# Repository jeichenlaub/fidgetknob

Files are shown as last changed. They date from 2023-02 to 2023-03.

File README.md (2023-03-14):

# Fidget Knob



Hello! Thanks for your interest in the Fidget Knob instrumented fidget object and research platform. This README serves as a general guide (or points you to other built-in and external guides) with all you need to know to construct and run your own implementation of the Fidget Knob. As such, I do implore you to read it carefully. 

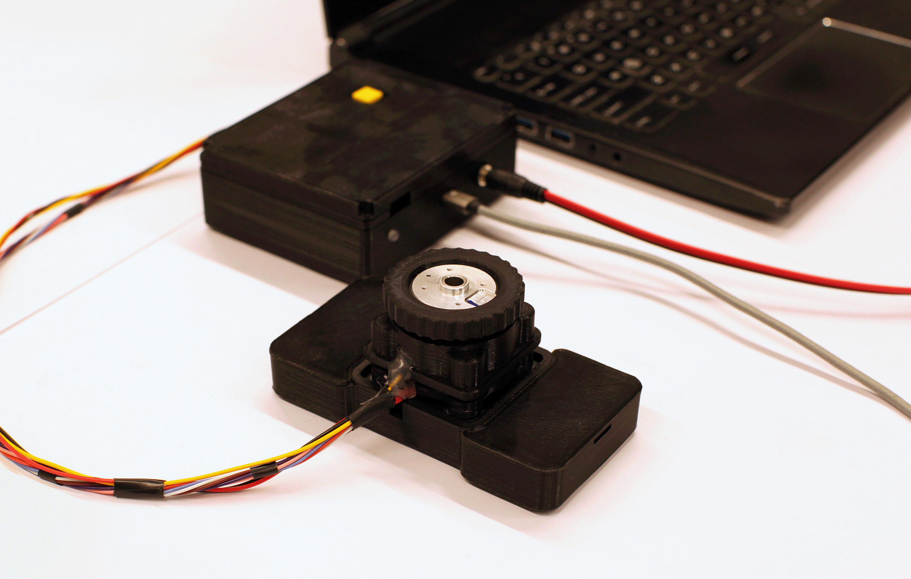
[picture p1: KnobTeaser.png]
Hero shot of the device


The overall system is pretty simple: a brushless DC (BLDC) motor has its angular position (and velocity) detected by a magnetic field sensor, which is fed into a ‘field oriented control’ algorithm to generate different haptic sensations and virtual detents. For those experienced in microelectronics, feel free to diverge from this guide when useful. For those still learning, hopefully this guide can take you step by step.

This GitHub repository contains all the files required from both a software and hardware perspective. It contains the following elements, and is organized in GitHub in a similar manner: 

# File Organization
 1. CAD\
&emsp;a. Part Files\
&emsp;b. Knob Assembly Instructions\
&emsp;c. Knob BOM\
&emsp;d. Knob Pics 
 2. Hardware\
&emsp;a. Electronics Assembly Instructions\
&emsp;b. Electronics BOM\
&emsp;c. Electronics Pics
 3. libraries\
&emsp;a. requirements.txt
 4. FidgetKnob_CustomCalibration.ino
 5. FidgetKnob_Main.ino
 6. FidgetKnob_DataLogging.pde
 7. LICENSE
 8. README

# Firmware and Software

The core of this project is a single Arduino .ino file. The software can be initiated in 2 modes: If one holds down the mode select button on startup (until the LED blinks blue 3 times), the Fidget Knob runs independently and without data logging enabled through Processing. If one does not hold any buttons, the Fidget Knob will remain uninitialized until it receives a timestamp from Processing, and it will flash green rapidly to indicate successful boot. While Arduino/C++ may not be the most robust programming language and platform for advanced works, it is relatively approachable for beginner and intermediate coders and thus suits our use case. 

This main .ino is supported by multiple libraries (found in requirements.txt) that are REQUIRED for the proper functioning of the software. These libraries are also included in the 'libraries' folder due to their permissive licensing rules.

**BEFORE RUNNING** the Fidget Knob, one must calibrate it with the included calibration program *FidgetKnob_CustomCalibration.ino.* Please note this calibration program is not great, and one should run it multiple times to get an average value for the "electrical offset." This value then needs to be changed in FidgetKnob_Main.ino file. The calibration program also should determine the amount of electrical pole pairs your motor has, but I find it best to do this using instructions on SimpleFOC's page for getting started (https://docs.simplefoc.com/example_from_scratch), or use the manufacturer claim. By setting this as a fixed value in the program, the 'electrical offset' calibration becomes more accurate. One can also use SimpleFOC's built in offset calibration programs, but these seem to yield equally inaccurate results with this specific hardware setup.

Datalogging is handled over serial connection with a parallel Processing scripts (FidgetKnob_DataLogging.pde). One can utilize this script either through the Processing IDE (running on a PC connected to the Fidget Knob via USB) or through the standalone application also included on this GitHub. Please note that certain parameters need to be adjusted (such as data file name and COM port of device) per instance of the Fidget Knob, so we highly recommend the former option of using the IDE. Complete instructions for the code, it's variables, and it's functions are found within the Processing file itself.

## Future Developments
We welcome any iterations that researchers and independent users wish to make for this prototype. We ask that you record these changes in a systematic way for future users.

A clear first point of future development is to enable either local or wireless data logging to untether the device from a laptop. The ESP32 platform is readily equipped to do so, and it was outside the scope of my own research.

The calibration programs are notoroiusly finicky and not fully functional. These need to be improved for this hardware combination to enable better off-the-shelf usage.

*insert more here when discovered*

# CAD
To build a full Fidget Knob, one will require a number of 3D printed parts to make up a housing for the knob and a container for the electronics. All of these files have been provided (as Solidworks .sldprt and print-ready .stl files) in the CAD folder.

While assembly of the parts is pretty straightforward, we have included a step by step instructions (KnobAssembly) and a bill of materials in the relevant folders.

# Potential FAQ and Troubleshooting
To save the general public some hassle, I have compiled a list of the largest and most crucial errors that I encountered while creating this device, as well as their solutions. This section can be a resource if something goes wrong, most specifically with compiling software and building out the electronic components of the project. 

*insert more here when discovered*

# Acknowledgments

This project is more or less a branch of Scott Bezek’s ‘[SmartKnob](https://github.com/scottbez1/smartknob)’ project , which is itself just a custom implementation of the [SimpleFOC](https://simplefoc.com/) library ([https://github.com/simplefoc](https://github.com/simplefoc)). We are greatly indebted to both of those projects and communities.

This project was developed during my term as a research employee at the faculty of Industrial Design Engineering at the Technical University of Delft in Delft, the Netherlands. As the project is based in open source software, no intellectual property rights are derived by the University.

# License and Citation

This Fidget Knob platform is designed for use in a research setting, ideally to enable better study of fidgeting behaviors and to help create target design interventions in this space. For those who use the Fidget Knob in their research, please cite this project with the following DOI: 10.5281/zenodo.7732484.

This project is licensed under Apache v2 (software, electronics, documentation) and Creative Commons Attribution 4.0 (hardware/mechanical) (see [LICENSE.txt](https://github.com/jeichenlaub/fidgetknob/blob/main/LICENSE)  and  [Creative Commons](https://creativecommons.org/licenses/by/4.0/)).
```
'fidgetknob' Copyright 2023 - John Anders Eichenlaub 

Licensed under the Apache License, Version 2.0 (the "License");
you may not use this file except in compliance with the License.
You may obtain a copy of the License at

		http://www.apache.org/licenses/LICENSE-2.0
		
Unless required by applicable law or agreed to in writing, software
distributed under the License is distributed on an "AS IS" BASIS,
WITHOUT WARRANTIES OR CONDITIONS OF ANY KIND, either express or implied.
See the License for the specific language governing permissions and
limitations under the License.
```

> Written with [StackEdit](https://stackedit.io/).

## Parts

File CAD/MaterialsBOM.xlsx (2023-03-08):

Item NO. | Part Name | Quantity | Example Link
----- | KNOB ASSEMBLY | ------ | MotorAssembly.sldasm
1 | FK_MT7601Holder | 1 | CAD
2 | FK_AssmBasePlate | 1 | CAD
3 | FK_TableBase | 1 | CAD
4
5 | FK_BLDCMount | 1 | CAD
6 | FK_AssmPeg | 4 | CAD
7 | FK_KnobGrip | 1 | CAD
8 | Super Glue (1g) | 1 | Your preferred brand
9 | Magnet (2x8mm dia.) | 8 | Neodymium magnet
10 | 30diax1mm washer | 52 | https://www.bilcastors.co.uk/product/flat-washer-10mm-internel-30mm-outter-x-1mm-thick/
11 | M3 hex head bolt, 10mm | 4
12 | Rubber Feet | 4-8 | https://www.westfloridacomponents.com/HW074/Clear+Hemispherical+Self-Adhesive+Rubber+Feet+Small+Bumpons+7.9++X++2.2mm.html
----- | Electronics Box | ------ | ElectronicsBox.sldasm
1 | FK_ElectronicsBox | 1
2 | FK_ElectronicsLid | 1
3 | FK_ButtonArm | 1
4 | Super Glue (1g) | 1 | Your preferred brand

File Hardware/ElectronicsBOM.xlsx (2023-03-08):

ID Number | Short Name | Official Name | Qty. | Links:
1 | Breadboard | Self-adhesive solderless breadboard, 0.1inch pitch |  | https://www.sparkfun.com/products/12002
2 | Breadboard | Self-adhesive solderless breadboard, 0.1inch pitch |  | "
3 | Motor Driver | TMC6300 BOB |  | https://www.top-electronics.com/en/breakout-board-with-tmc6300
4 | Microcontroller | DoIt Devkit ESP32 v1 |  | https://nl.aliexpress.com/item/32928267626.html
5 | BLDC Motor | Brushless DC motor TYPE A, 260 KV, 7 pole pair, 32mm diameter |  | https://nl.aliexpress.com/item/1005004385440039.html
6 | Magnetic Encoder | MT6701 (MagnTek) BOB |  | https://nl.aliexpress.com/item/1005004216051325.html?gatewayAdapt=glo2nld
7 | Resistor 1 | 560 ohm
8 | Resistor 2 | 560 ohm
9 | 24AWG coated wire (65cm) |  | 20
10 | Mode Switch Button | Basic 4 pin button (omron b3f) |  | https://www.sparkfun.com/products/10302
11 | Indicator LED | 4 Pin translucent RGB LED |  | https://nl.aliexpress.com/item/1005004948808839.html?
12 | DC Supply Jack | Standard barrel jack, 2 output pins version |  | https://nl.aliexpress.com/item/4000648876487.html?curPageLogUid=6nWUYysneIPZ
13 | Power Supply | AC to DC power supply, 10v 2 amp |  | https://nl.aliexpress.com/item/1005003090719320.html?curPageLogUid=LcfFNOlMRHSw
14 | Micro USB cable | 1m Micro-USB to USB A cable |  | https://nl.aliexpress.com/item/4000115356367.html?scm_id=1007.13339.291025.0&scm-url=1007.13339.291025.0
15 | Wisher jumper wire kit |  |  | https://www.retroamplis.com/Jumper-set-350-pcs

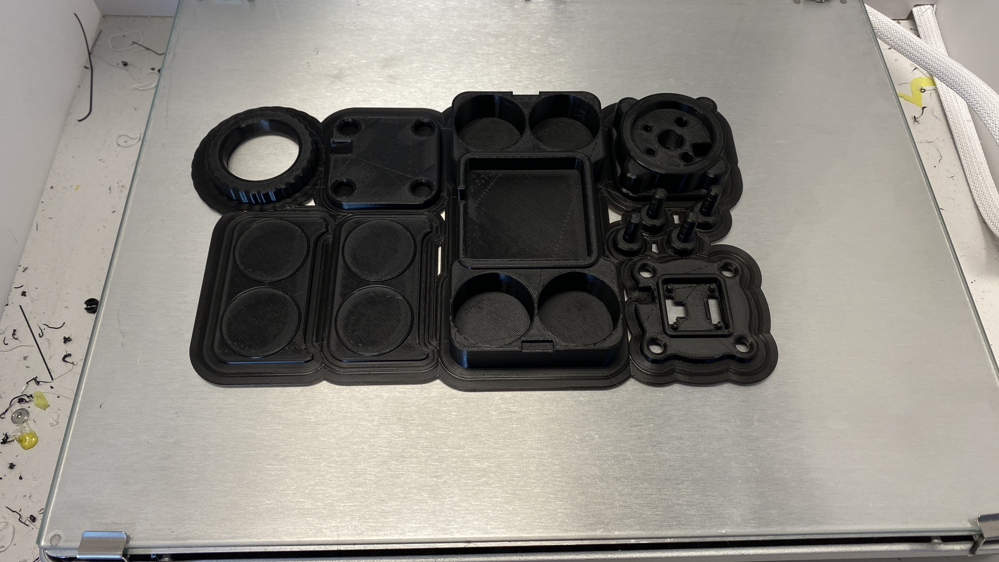
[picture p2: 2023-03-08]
CAD/KnobPics/Parts_OnPrinter.jpg

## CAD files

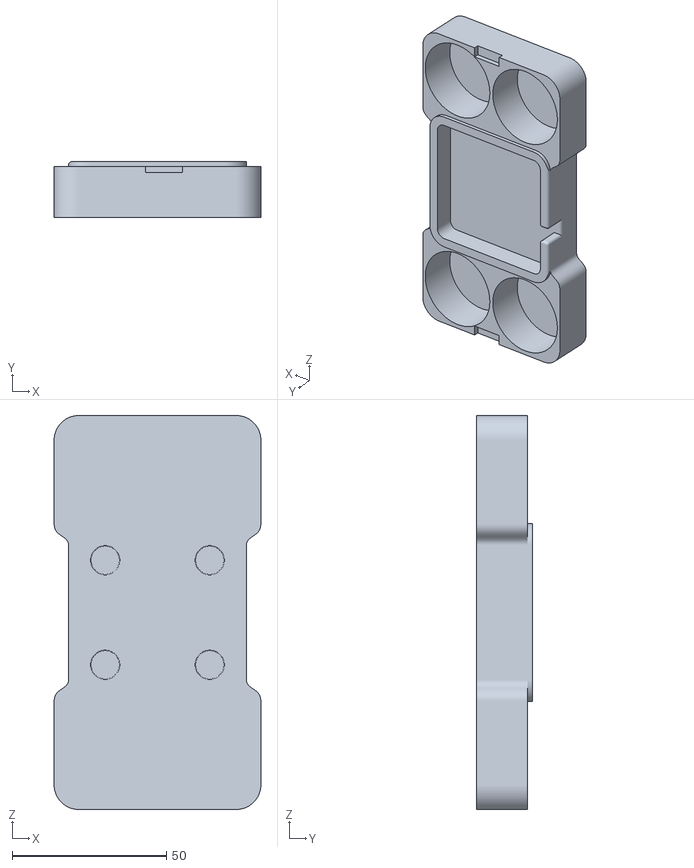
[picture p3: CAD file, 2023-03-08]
CAD/MotorAssembly - FK_TableBase-1.STL
67.0 x 18.0 x 127.7

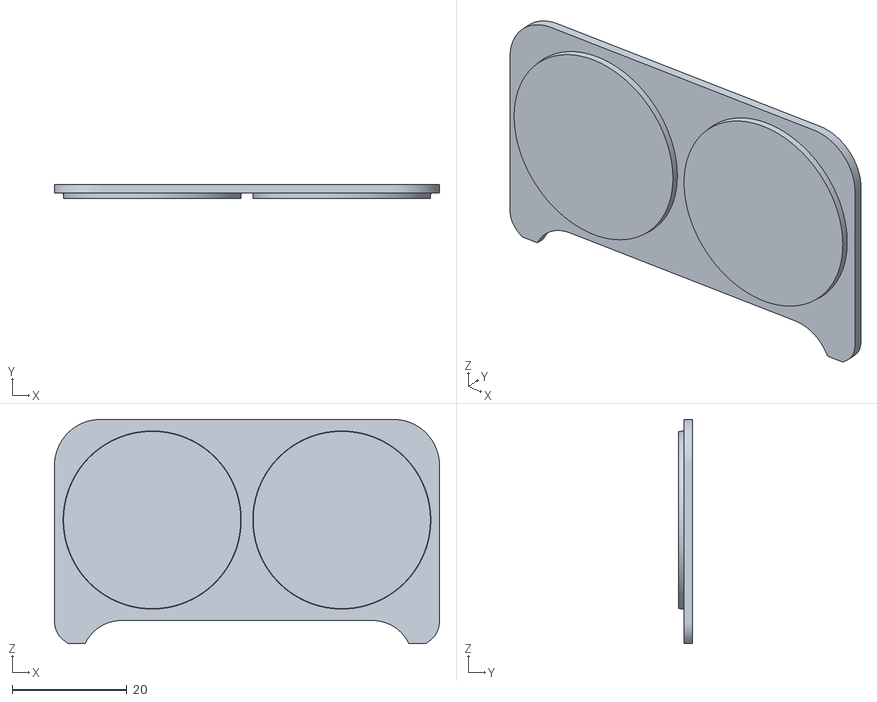
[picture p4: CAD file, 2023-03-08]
CAD/MotorAssembly - FK_TableBase_Lid.STL
67.0 x 2.50 x 39.0

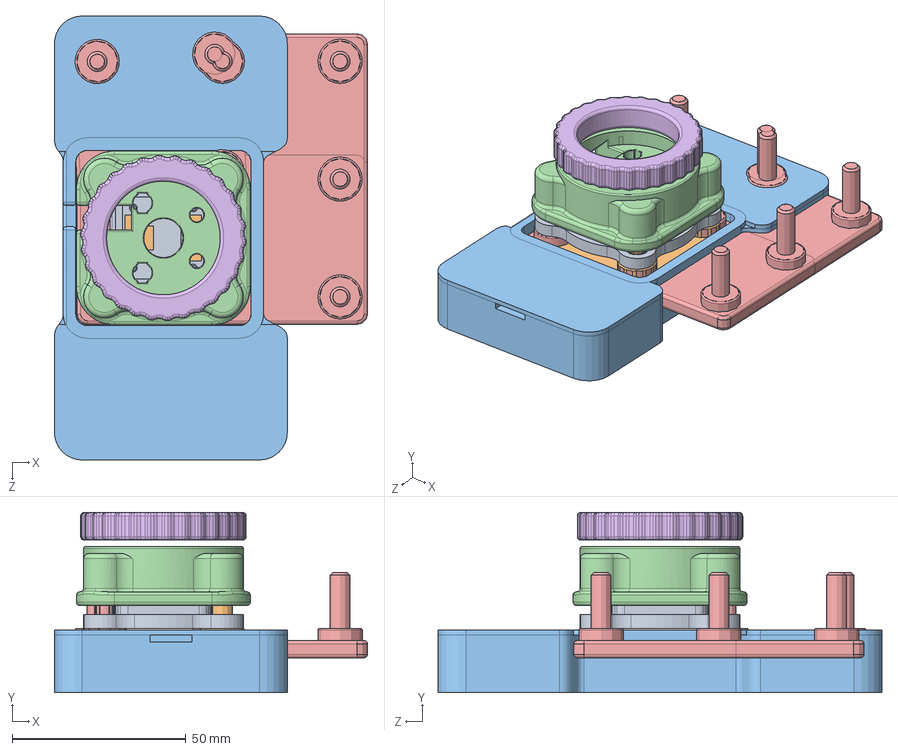
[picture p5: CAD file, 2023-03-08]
CAD/MotorAssembly.SLDASM
90.1 x 51.8 x 127.7 mm
FK_MT6701Holder
FK_AssmBasePlate
FK_TableBase
FK_BLDCMount
FK_AssmPeg x 4
FK_KnobGrip

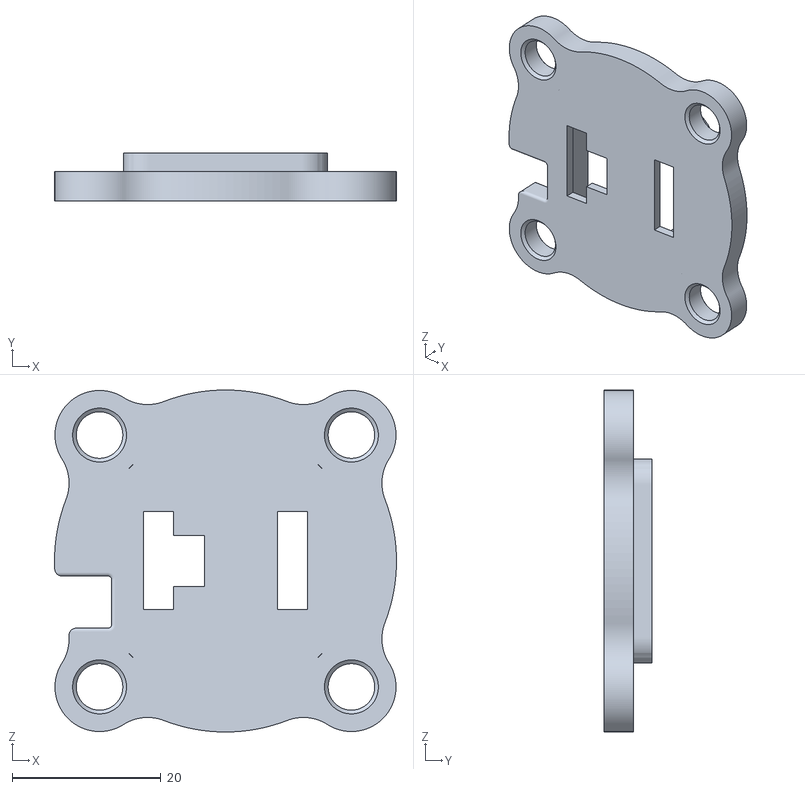
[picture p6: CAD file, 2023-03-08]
CAD/MotorAssembly - FK_MT6701Holder-1.STL
46.0 x 6.50 x 46.0

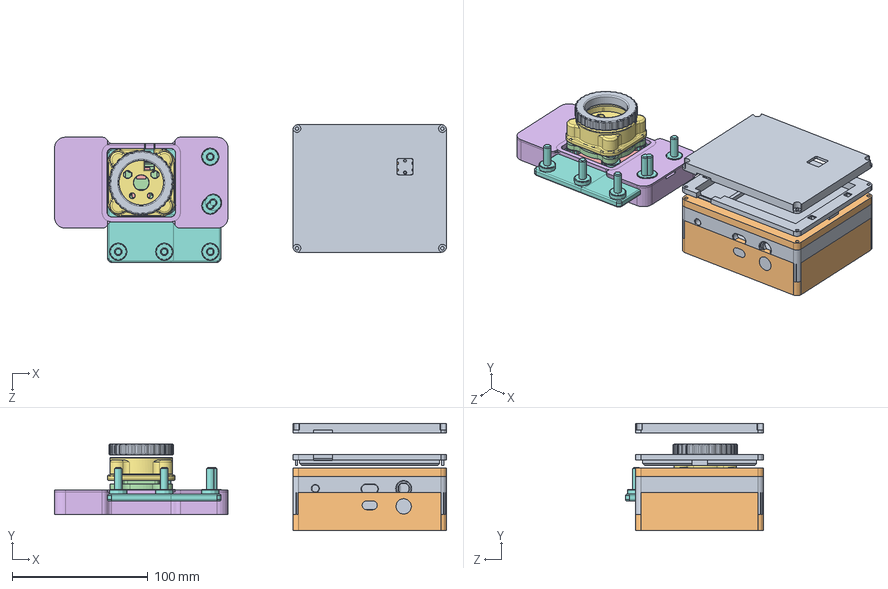
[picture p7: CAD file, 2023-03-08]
CAD/FK_CompleteAssm.SLDASM
288.4 x 79.0 x 101.5 mm
FK_ElectronicsBox
FK_ElectronicsLid
FK_ButtonArm
FK_MT6701Holder
FK_AssmBasePlate
FK_TableBase
FK_BLDCMount
FK_AssmPeg x 4
FK_KnobGrip

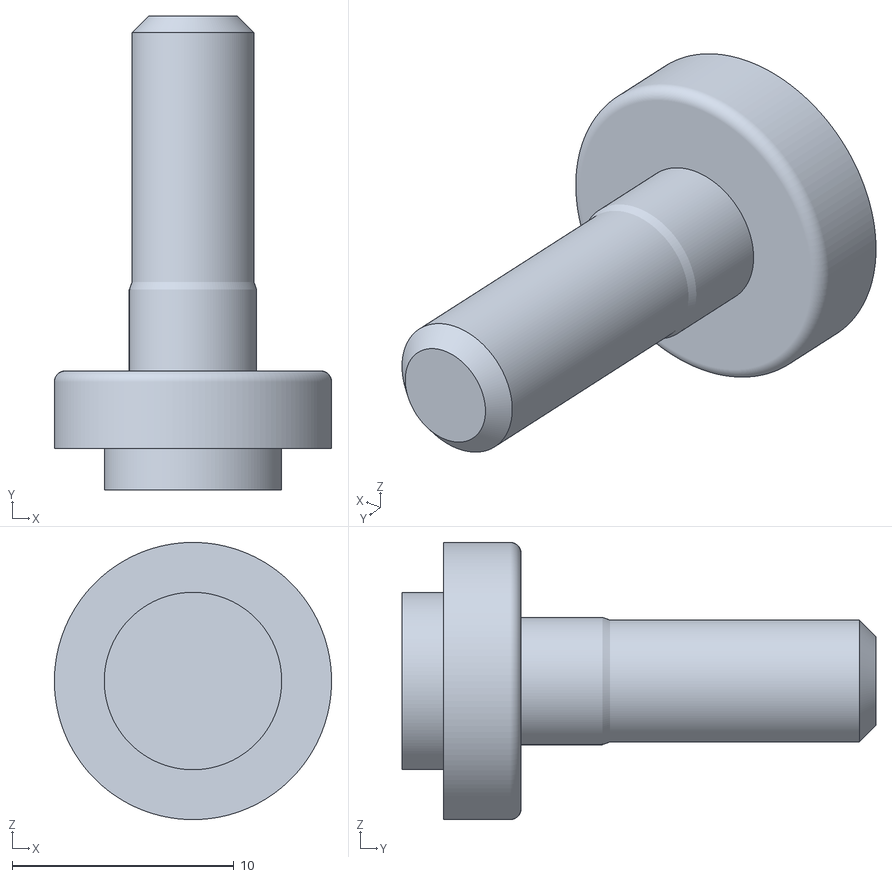
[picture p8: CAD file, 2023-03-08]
CAD/MotorAssembly - FK_AssmPeg-1.STL
12.5 x 21.4 x 12.5

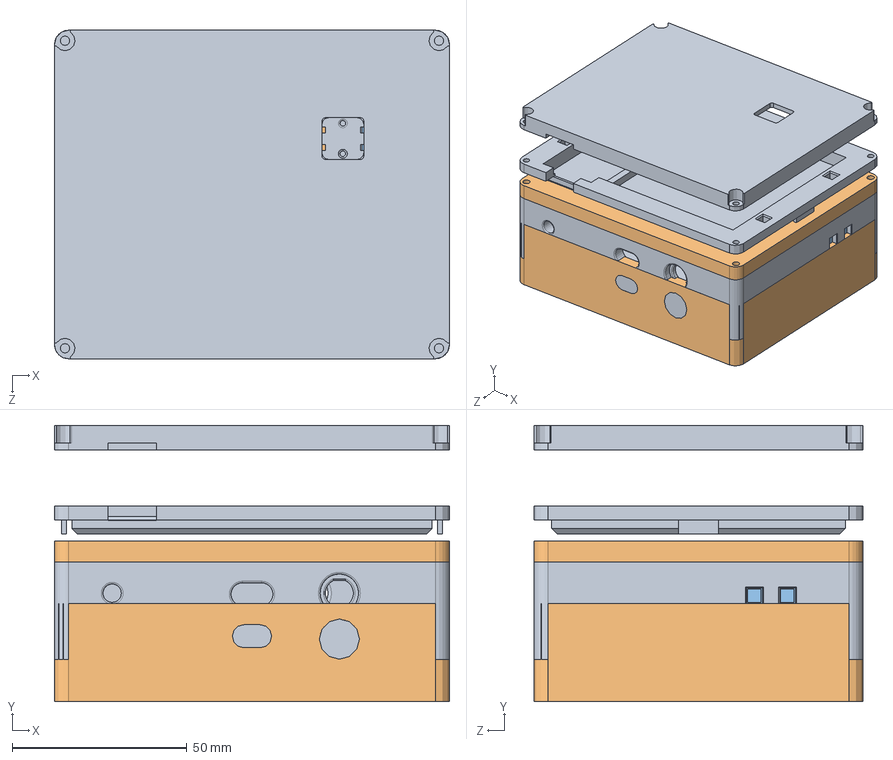
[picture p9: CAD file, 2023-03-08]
CAD/ElectronicsBox.SLDASM
113.0 x 79.0 x 94.0 mm
FK_ElectronicsBox
FK_ElectronicsLid
FK_ButtonArm

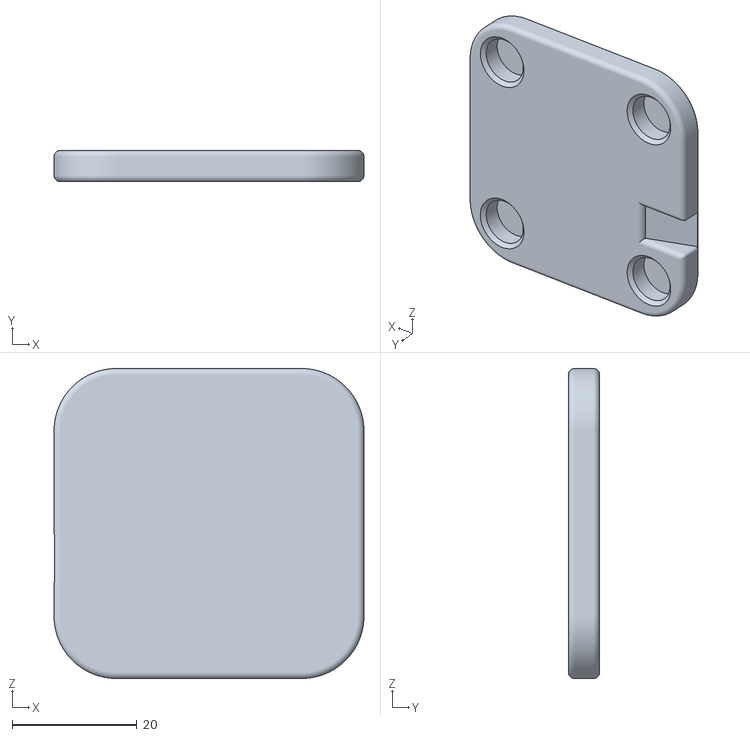
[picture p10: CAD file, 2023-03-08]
CAD/MotorAssembly - FK_AssmBasePlate-1.STL
49.7 x 5.00 x 49.7

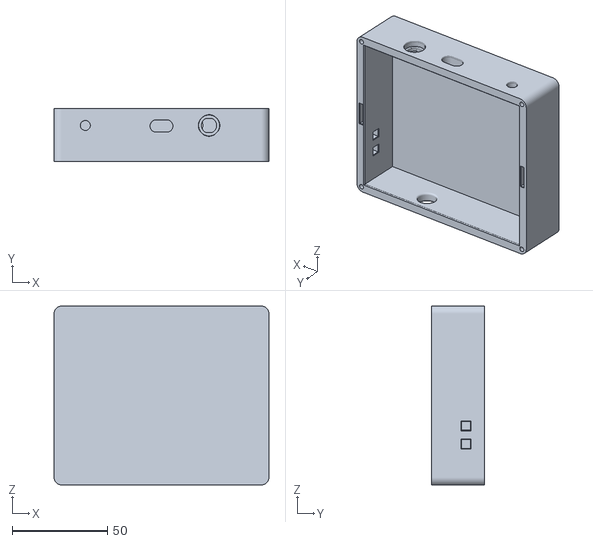
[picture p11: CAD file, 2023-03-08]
CAD/ElectronicsBox - FK_ElectronicsBox-1.STL
113.0 x 28.0 x 94.0

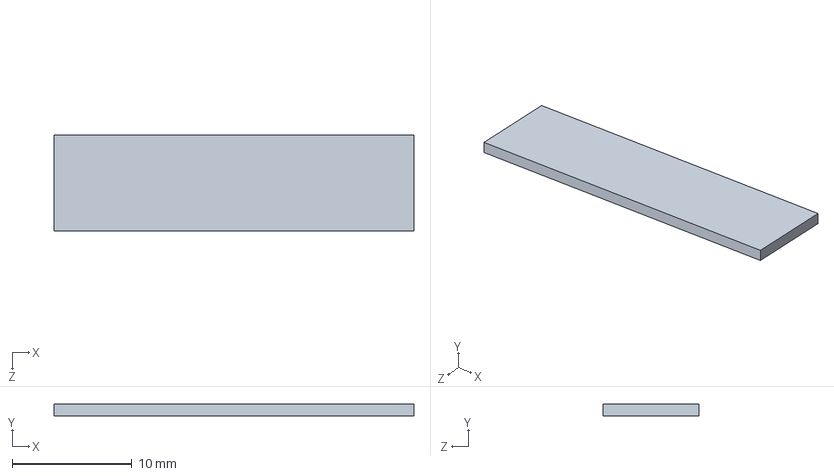
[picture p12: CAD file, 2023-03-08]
CAD/FK_Spacer.SLDPRT
30.0 x 1.00 x 8.00 mm

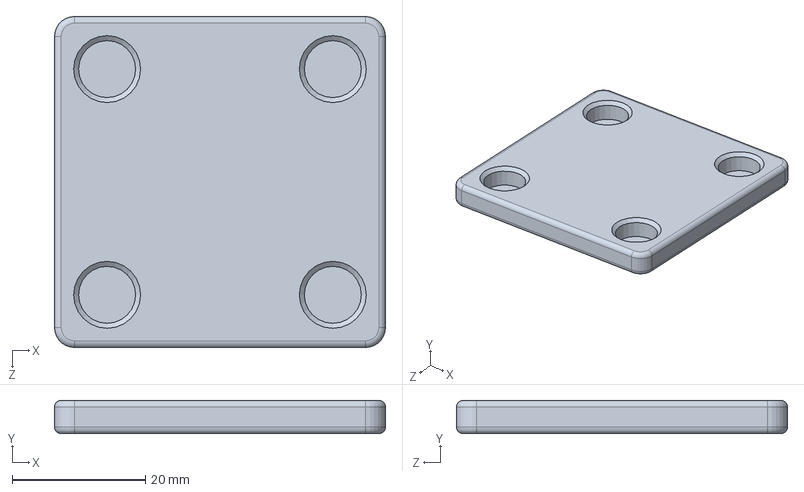
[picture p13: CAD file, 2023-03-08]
CAD/FK_AssmBasePlate.SLDPRT
49.7 x 5.00 x 49.7 mm

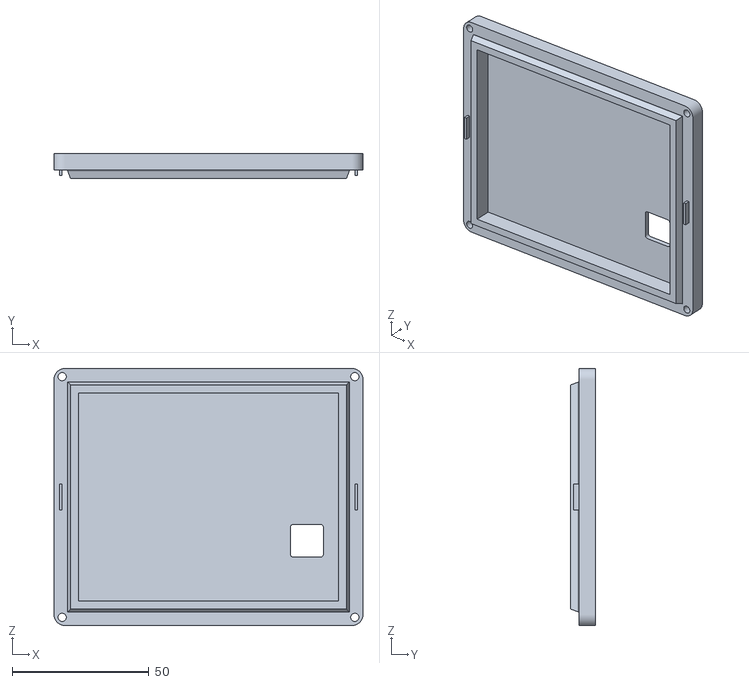
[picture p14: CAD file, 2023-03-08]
CAD/ElectronicsBox - FK_ElectronicsLid-1.STL
113.0 x 9.00 x 94.0

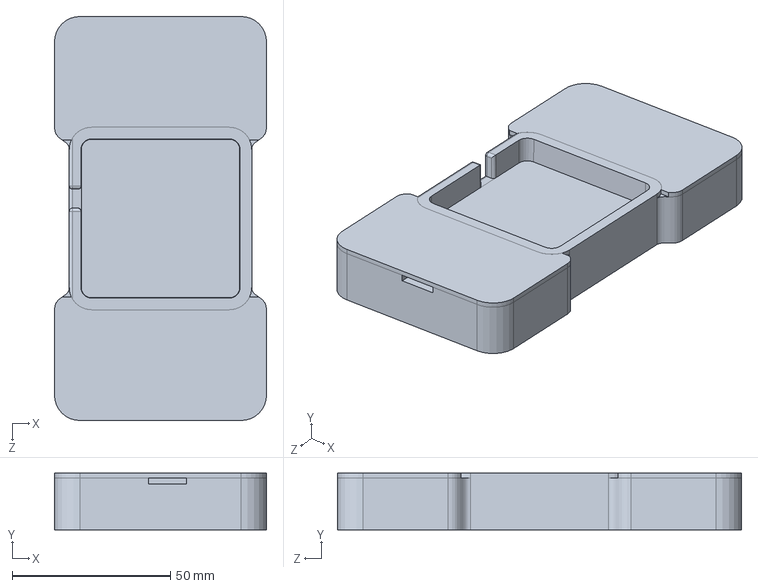
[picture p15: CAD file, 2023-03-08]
CAD/FK_TableBase.SLDPRT
67.0 x 18.0 x 127.7 mm

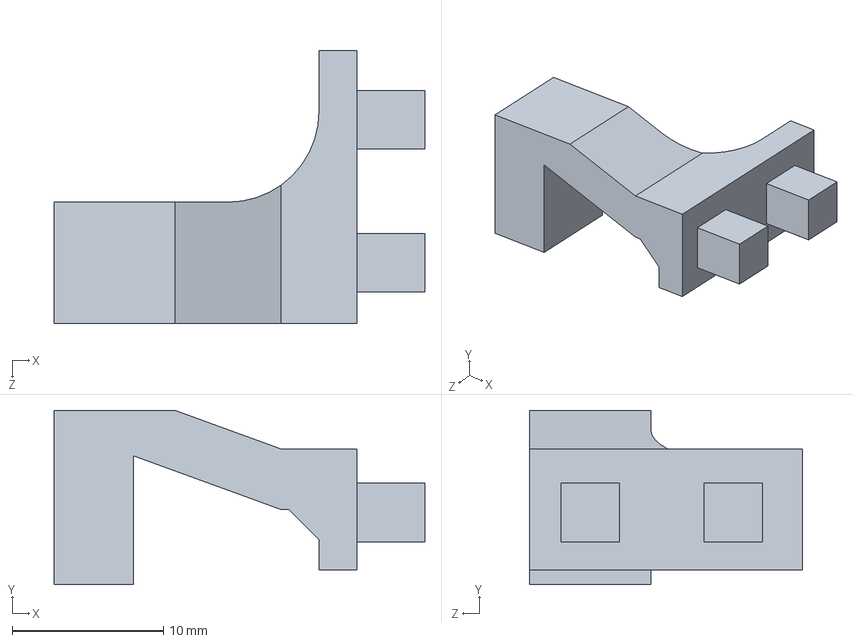
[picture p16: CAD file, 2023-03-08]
CAD/FK_ButtonArm.SLDPRT
24.5 x 11.5 x 18.0 mm

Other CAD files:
CAD/FK_TableBase_Core.STL
CAD/FK_ElectronicsBox.SLDPRT
CAD/FK_TableBase_Lid.STL
CAD/FK_AssmPeg.SLDPRT
CAD/ElectronicsBox - FK_ButtonArm-1.STL
CAD/FK_BLDCMount.SLDPRT
CAD/FK_ElectronicsLid.SLDPRT
CAD/FK_KnobGrip.SLDPRT
CAD/FK_MT6701Holder.SLDPRT
CAD/FK_Spacer.STL

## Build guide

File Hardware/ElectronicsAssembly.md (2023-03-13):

# Electronics Assembly
As the title suggests, the following is a step-by-step guide (with pictures!) for assembling the electronic components of the Fidget Knob project. Enjoy!

First, we’ll build the basis of the electronics box.
## Electronics Box

1.  Begin with the FK_ElectronicsBox 3D printed part.

2.  Take one of the two breadboards and remove the right-hand power rail unit from the board (2 columns of holes)\
&emsp;a. This board becomes the leftmost board in the assembly.

3.  Add the other breadboard to the right half of the box.

4.  Place the TMC6300 BOB 1 row from the top, with the right-side pins in the first column (A) of the right-side breadboard,

5.  Add the brown wires as demonstrated in the image below. All brown wires run to the blue ‘GROUND’ power columns.

6.  Add the white and green/red combo wires (same image). These run from the VCC rails.\
&emsp;a. Important note: later, one rail (right) will be powered by 3.3V and the other (left) 5v. Do not bridge these rails.

7.  Now we place the red wires for the microcontroller to TMC motor driver board.\
&emsp;a. Starting with the lowest down wire, we place one end in F23 and the other in F9.\
&emsp;b. We continue with the next wire up, connecting F22 to F8.\
&emsp;c. Connect the remaining 4 red wires in similar sequence.\
&emsp;d. Do your best to arrange the jumper wires neatly and flatten their overlapping points a bit to avoid vertical forces on the jumper wires themselves.

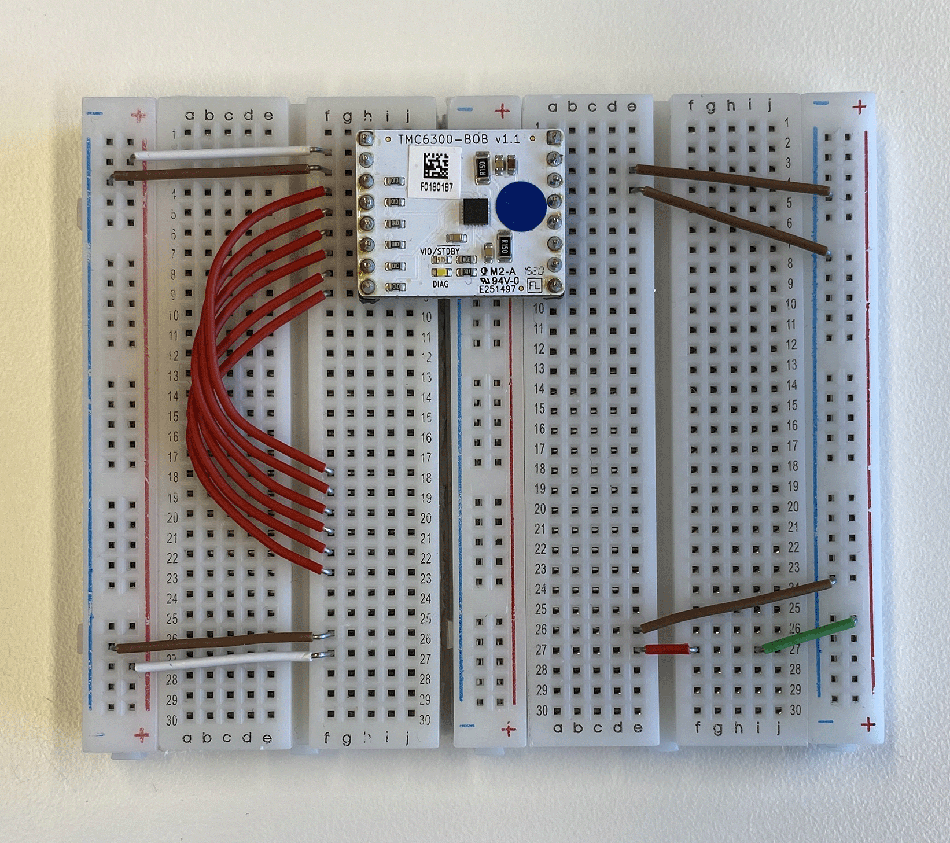
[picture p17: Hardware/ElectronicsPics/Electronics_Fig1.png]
Basic breadboard connections and TMC6300


8.  Prepare the DC power supply jack with ~9cm length, 22AWG wire in red and black.\
&emsp;a. Secure it to the electronics housing and connect positive and ground wires to breadboard I1 and I3, respectively.
9.  Prepare the 4-pin RGB with associated wires and a 560 ohm resistor (Resistor 1) (see picture 2).\
&emsp;a. Some RGB LEDs are common anode, others are common cathode. This will change your pinout and resistor setup. Please modify as you need!\
&emsp;b. Connect up the RED pin to F25 and GREEN to F24, and leave the positive line and BLUE wire unconnected.

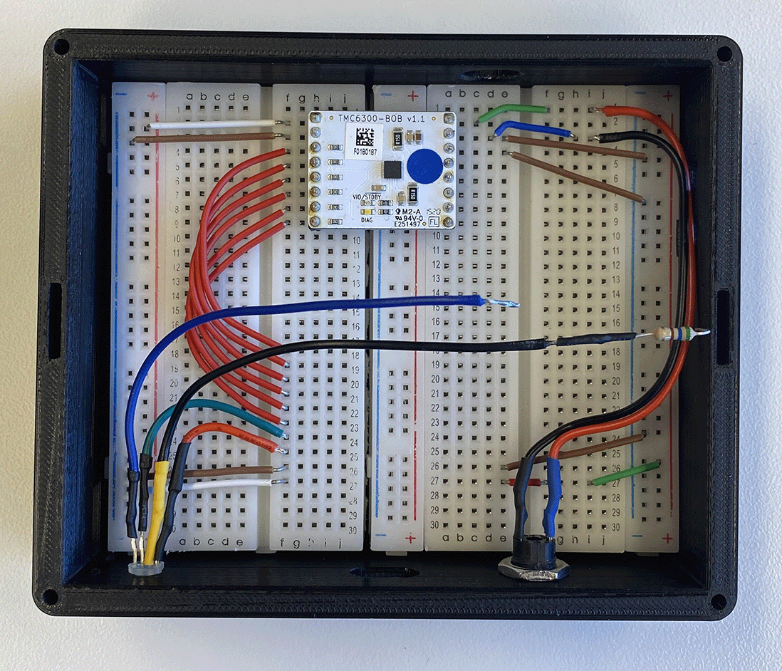
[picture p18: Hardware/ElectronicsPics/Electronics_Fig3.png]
Breadboard in casing with LED and power supply wired up
 

10.  Place the DoIt DevKit v1 ESP32 development board into both of the breadboards, with the top left EN pin in slot H13 and the 3v3 pin in B27.\
&emsp;a. Please test the board in advance with a simple blink example program in the Arduino examples (and check solder connections to pins!)\
&emsp;b. The USB port should be aligned to the opening on the front of the case. Check this now!

11.  Plug in the BLUE and positive voltage lines from the LED into D23 and the right most power rail, respectively. These will cross over the top of the ESP32 board.

## Fidget Knob Itself

12. **IMPORTANT** The MT6701 magnetic sensor must be enabled in SPI mode. If you purchased the same board as I used, you need to solder a bridge between two pins to select SPI (instead of I2C). See **RED MARKS** in image below.

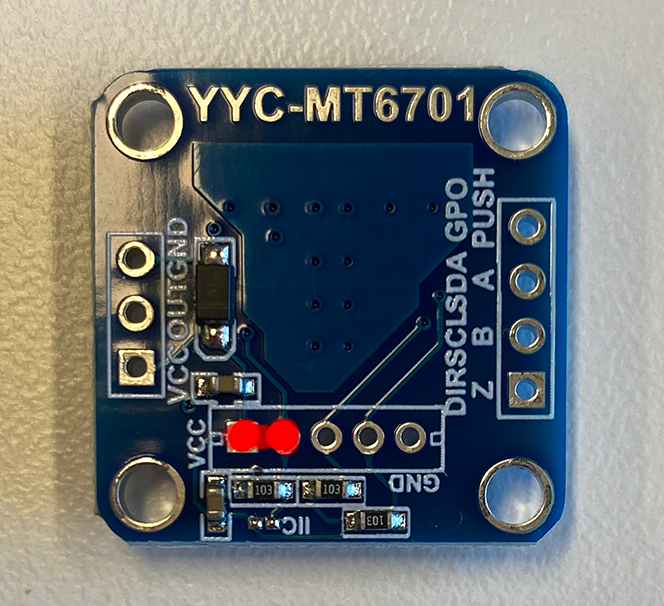
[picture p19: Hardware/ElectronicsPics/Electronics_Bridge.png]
Please bridge the two red pins!
 
 
13. Solder 7 wires to the magnetic encoder sensor to all available pins on the breakout board. Not all are used for data transmission, but it is smart to ground unused pins to avoid floating and accidental triggering.\
&emsp;a. We used a length of 24AWG wire at approximately 65cm for each, but you can choose to shorten this if desired. Anything above 1 meter length risks data packet loss and transmission issues.\
&emsp;b. **Now do step 3 of the Knob Assembly guide**, attaching the MT6701 sensor board to it's 3D printed housing. This involves feeding the wire bundles through the holes in the housing as seen in the image below.\
&emsp;c. I chose to twist these wires into 2 bundles (one for each side of the breakout board) to make sure they could not be overly bent or destroyed, and secured it with heatshrink tubing. This is optional but makes the device cleaner and more robust, and will slightly shorten the effective wire bundle length.

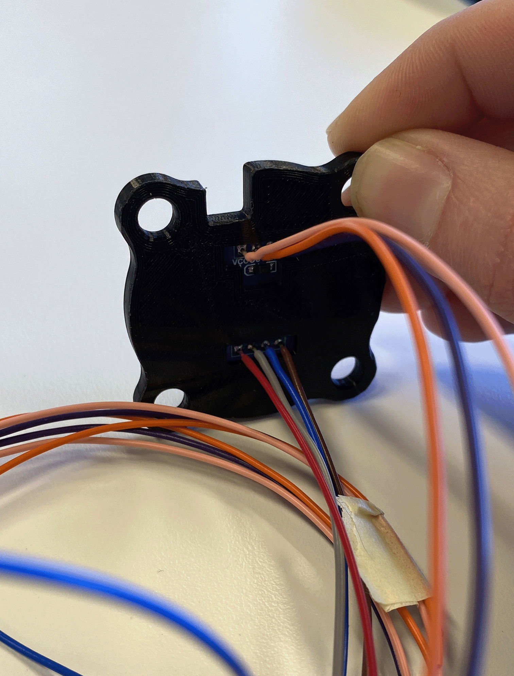
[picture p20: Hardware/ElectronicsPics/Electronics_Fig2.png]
image info
    

14.  Attach the motor wires.\
&emsp;a. If using the exact motor from my BOM, you will have to cut off the micro connector and solder wires directly to the 3 *very thin* wires exiting the motor. Please exercise utmost caution with this step to secure stable connection. Tinning both wires in advance and later heatshrink wrapping is advised.\
&emsp;b. **Now do step 6 of the Knob Assembly Guide** For the motor, this can be done before OR after step 14.c, below, of bundling the wires.\
&emsp;c. Again, we used 24AWG wire at a length of 65cm for each of the three connections. These lines were then twisted into a bundle and secured with bands of heatshrink tubing.
   
 ## COMBINE PARTS ##  
15.  Once all of the wires are prepared, we can unit the knob assembly and the base electronics box together. **IMPORTANT** please feed all of the wires through the passthrough in the back of the electronics box before starting soldering, otherwise you will not be able to build the device correctly.\
&emsp;a. Please see the below image for a clear view of how everything is wired together.

16. The motor wire bundle can be trimmed about 3-5cm shorter than the wire bundles for the magentic sensor, and should be attached to the following pins:\
&emsp;a. RED to breadboard position A5, soldered directly to TMC6300 pin.\
&emsp;b. YELLOW to A6, "	"	"	"\
&emsp;c. BLACK to A7

17. The two wires bundles for the magnetic sensor can then be added to the breadboard and microcontroller, soldering the Z, B, and A wires and adding the rest to the breadboard.\
&emsp;a. *Hint*: to secure a better connection for the wires entering the breadboard, tin the trimmed ends with solder to make them slightly thicker and more resistant to bending.

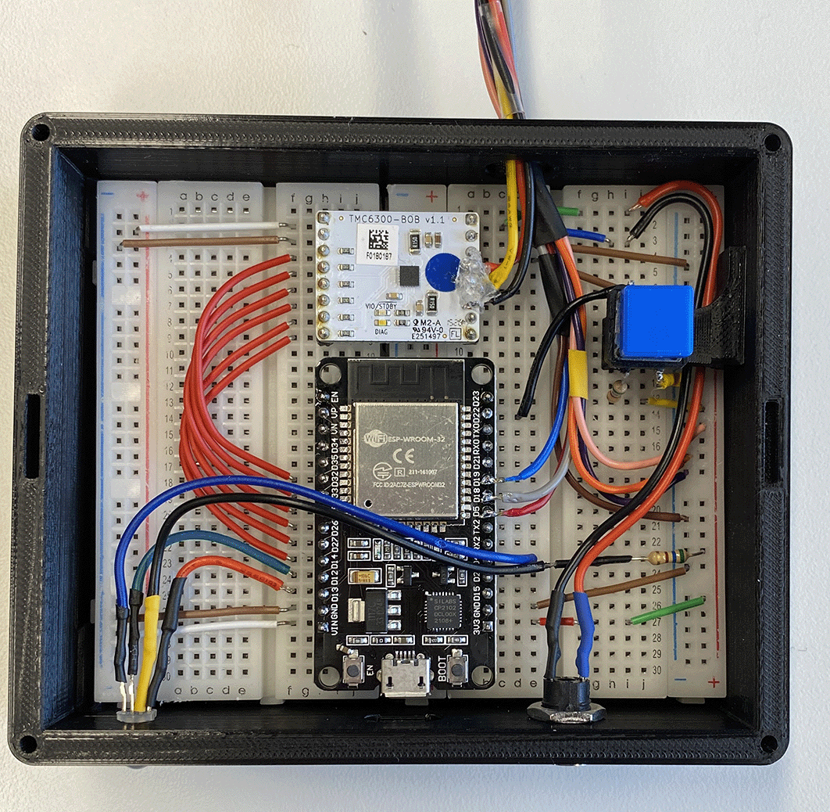
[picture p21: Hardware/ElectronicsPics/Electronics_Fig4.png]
All connections wired up properly.
   

18. We can now add the pushbutton support arm to the casing (FK_ButtonArm), being careful not to pinch the DC power supply wires against the wall. Please use some adhesive to guarantee the support arm does not move out of position.

19. Add connections to the pushbutton as shown in the following image, with a 560 ohm resistor from the +3v3 volt rail, a black wire to ground, and colored one to breadboard position D14.\
&emsp;a. After securing these appropriate length connections, place the lid (FK_ElectronicsLid) on the box, align the pushbutton on it's support structure, and secure the button underneath with adhesive.\
&emsp;b. Remove the lid.

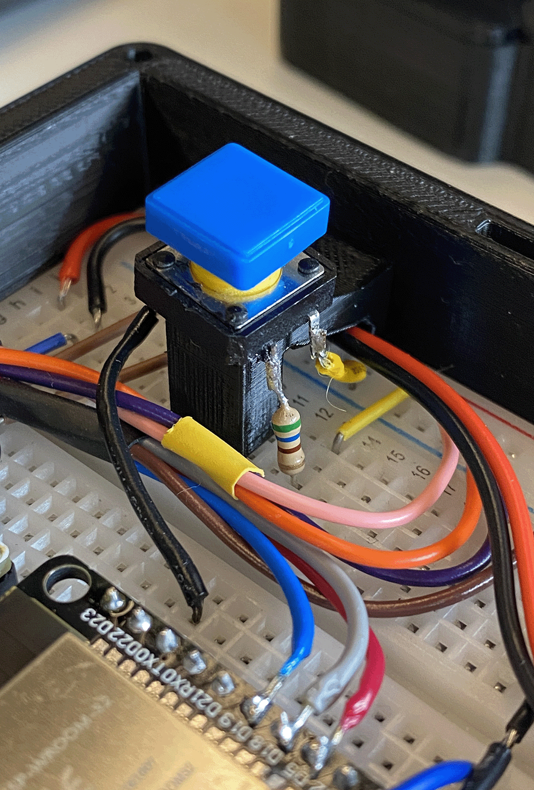
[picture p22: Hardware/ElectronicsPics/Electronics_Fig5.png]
Closeup of the pushbutton wiring and assembly.
   

20. Time to double check your work. Use the table and reference image below to compare your own device!

21. Time to flash the ESP32 with the calibration code and then the real Fidget Knob program! Happy fidgeting and research.
    
**Overall Connection Table**
| Wire/Connection From Component | ESP Pin                    |
|--------------------------------|----------------------------|
| LED – Red                      | ESP32 pin D13              |
| LED – Green                    | ESP32 pin D12              |
| LED – Blue                     | ESP32 pin D4               |
| LED - +voltage                 | Right Power Rail           |
| DC Supply – Red (+ voltage)    | Breadboard I1              |
| DC Supply – Black (Ground)     | Breadboard I3              |
| Button - Signal                | ESP32 pin D22              |
| Button - +voltage              | Right Power Rail           |
| Button - Ground                | Right Ground Rail          |
| Motor – Red                    | TMC Pin 12 (Phase U) in A5 |
| Motor – Yellow                 | TMC Pin 13 (Phase V) in A6 |
| Motor – Black                  | TMC Pin 14 (Phase W) in A7 |
| MT6701 - VCC                   | Right Power Rail (3.3v)    |
| MT6701 - OUT                   | Ground                     |
| MT6701 - GND                   | Ground                     |
| MT6701 - Z                     | ESP32 pin D5               |
| MT6701 - B                     | ESP32 pin D18              |
| MT6701 - A                     | ESP32 pin D19              |
| MT6701 - Dir                   | Ground                     |

> Written with [StackEdit](https://stackedit.io/).

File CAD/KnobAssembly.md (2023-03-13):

# Instructions for Assembly and Printing 

Generally speaking, the printing process should be quite ‘plug and play’ with minimal adaptations required. Obviously, if you use different circuit boards or BLDC motors, the dimensions will have to be adjusted. This is why we include both STL files ready for printing and the original Solidworks files.

Below are some of the specifications used for printing the existing version:

 - Printer: Ultimaker S5, staged in Cura
 - Material: Basic non-branded PLA, black. 0.4mm nozzle
 - Temperature: 205c for hot end, 60c for build plate
 - Layer Height: Between 0.1mm and 0.2mm layer height. We used 0.15mm.
 - Infill: Nothing more than 20% is necessary, we used 18% on the ‘gyroid’ setting.
 - Support and Adhesion: Support structures for overhangs, 8mm skirt for adhesion.

All parts should be printed exactly at their built size (100% scale), as certain dimensions have already been adjusted to account of tolerances and minimal shrinkage while printing.

The **one** exception to this is the ‘Knob’ part. The inner diameter is intentionally a hair too small, and thus one will need to scale this knob up for a perfect ‘force fit’ with your BLDC motor. We found around 100.5% or 101% of the original size worked. Of course, your mileage may vary based on your material choice, print speed, build environment temperature, and other factors. Adjust and test as suits your use case!

All parts are to be printed one time, with the exception of the pins (4 instances).

## Assembly Steps - Knob Unit 

 1. Take the part FK_AssmBasePlate as the first component, and take 4 round magnets to insert into each hole. Use a 5th magnet on the underside of each to orient all the magnets with the same polarity.

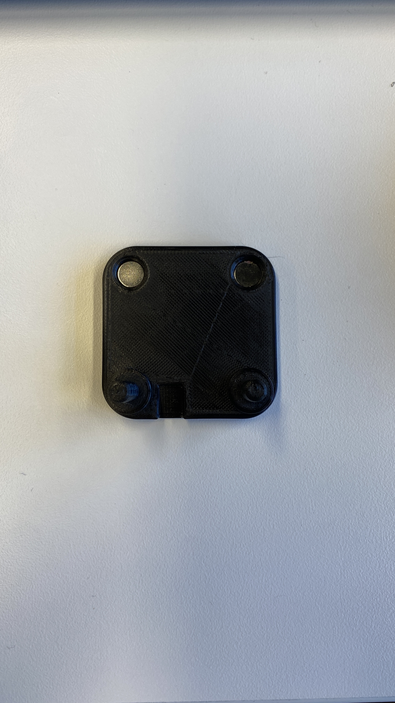
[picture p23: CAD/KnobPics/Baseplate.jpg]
View of first baseplate piece with 1 magnet inserted
 

 2. Take the 4 copies of FK_AssmPeg and, using superglue, adhere above the holes with the magnets. One could glue the magnets themselves into the holes if you desire.\
&emsp;a. One could also use one of the next parts in the stack (FK_MT6701Holder or FK_BLDCMount) the keep these pins aligned with proper tilt while the glue dries.

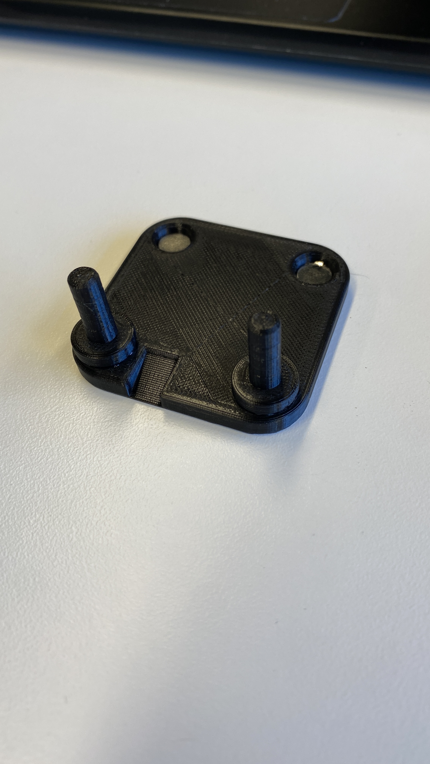
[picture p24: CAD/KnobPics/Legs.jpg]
Baseplate with 2 of 4 legs inserted and glued
 

 3. Take the prepared MT6701 magnetic sensor and wires and insert it into the FK_MT6701Holder housing, feeding through the wires. Pay attention to orientation, as the cutouts allow space for underside resistors to help the board lay flat.\
&emsp;a. After this step, the wires can be bundled.

 5. Attach the parts from step 4 to the cured AssmBasePlate, using small amounts of super glue on the larger diameter of each pin to secure the housing. Press down firmly to guarantee parallelism.

 6. Take the prepared BLDC motor and wires from step 14 of the electronics assembly guide and add this to FK_BLDCMount (and then both to the built of stack of parts from steps 1-5). Again, utilize small amounts of glue, this time hot glue, in the mounting holes of the housing, to secure items together.\
&emsp;a. **Make sure the all wires are facing the same orientation and match with the cutouts designed into the parts.**

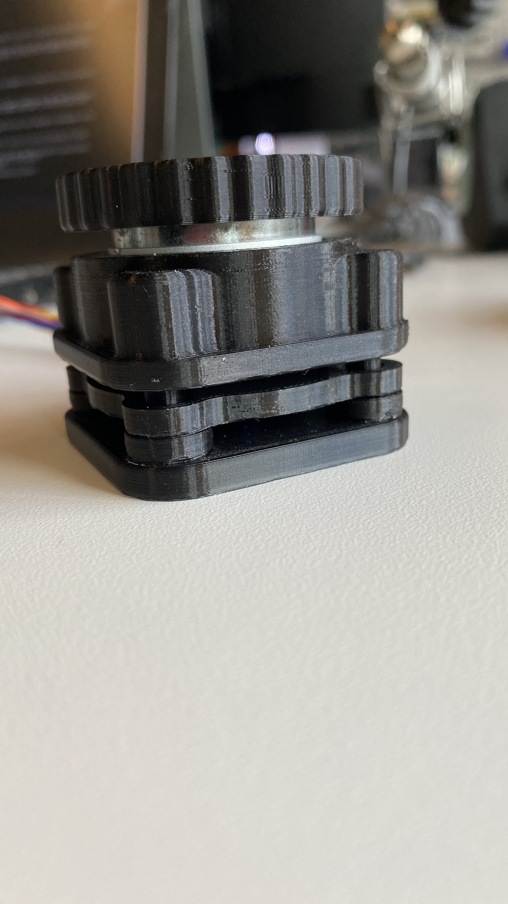
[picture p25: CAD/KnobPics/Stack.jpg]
Knob unit assembly all stacked together and fitting flush
 

 7. Now, all of the wire bundles can themselves be bundled together using heat shrink tubing or whatever fastening mechanisms you prefer.

## Assembly Steps - Table Base 

 1. Take FK_TableBase and fill each of the 4 cylindrical holes with 12 washers (30mm diameter, 1mm thickness).

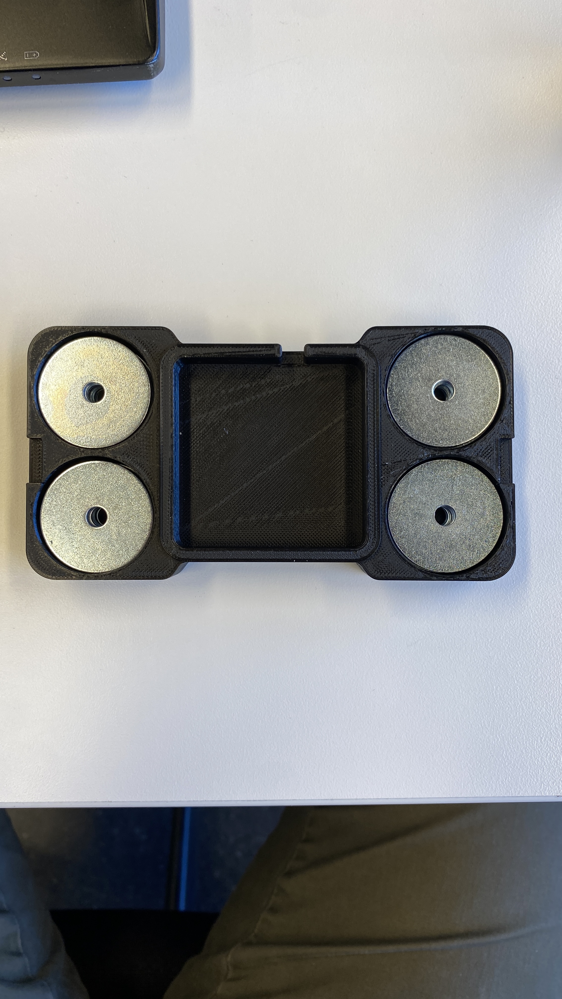
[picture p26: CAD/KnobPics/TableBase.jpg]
Table base part with weight washers
  

 2. To avoid noise and movement, these washers can be centrally filled with hot glue.

 3. After the washers are inserted, the 2 FK_ElectronicsLid parts can be used to cover the washers.\
&emsp;a. While these are pretty secure by themselves, we recommend super or hot glue to fasten them down permanently.

 4. After these components are dried and adhered, flip the parts over to reveal the magnet holes on the bottom.

 5. You can choose how many magnets to place in the device t ovary the attractive force between the knob assembly and this base for the table top (we personally used 2).

 6. Place the knob assembly from the prior section into place on the FK_TableBase, and THEN insert the magnets into the deep holes, as this will properly align their polarity.

 7. Follow the magnets with generous hot glue to seal the holes. Let dry.

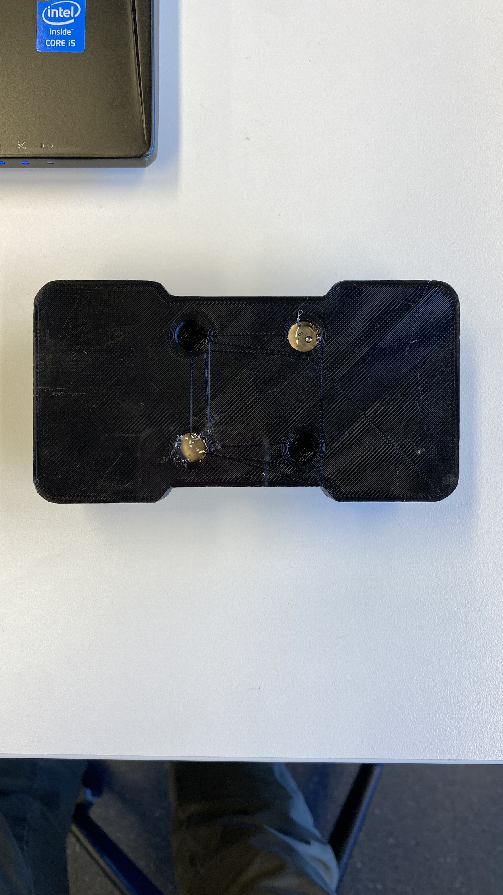
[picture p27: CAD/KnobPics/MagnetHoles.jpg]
Bottom side of table base part showing magnet holes
  

 8. Flip right-side up and test the removal force of the knob assembly from the base. is it not strong enough? Add a 3rd (and 4th) magnet to the base part.

*This should mark the full assembly of all parts!*

> Written with [StackEdit](https://stackedit.io/).

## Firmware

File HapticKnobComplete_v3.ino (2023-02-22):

/*  A custom example of SmartKnob (and therefore SimpleFOC software) that contains all critical code to run the Fidget Knob within one .ino file.
    This program is subdivided into relevant classes for setup, configuration, data output/monitoring, and the actual haptic sensation.

    PINS:
    Obviously, your setup may differ from my own as it relates to the exact pin assignments for different components.
    I have tried to collect all relevant pin assignment variables at the top of the file TO BE CHANGED by each user and implementation.
    Other variables, such as maximum supply and driver voltage, can be changed within the program.
    
    DATA:
    This code also monitors key variables and outputs them to the serial terminal. These variables are internally averaged and filtered to create less output samples.    
    Further, we are not using built in 'monitoring' function as it is harder to customize the output and maneuver variables to our liking.
    The data output to the serial terminal is read by a separate Processing script. The original design logged files over a SPI SD card, but this was incompatible with the Fidget Knob haptic feedback.

    
*/
#include <SimpleFOC.h>
#include "Arduino.h"
#include <analogWrite.h>
#include <vector>
#include "SimpleFOCDrivers.h"
#include "encoders/MT6701/MagneticSensorMT6701SSI.h"
#include <sys/time.h>

// KEY VARIABLES TO BE CHANGED BY USER
static int configNumber = 9; //Total number of Fidget Knob mode configurations!

// ********************HAPTIC KNOB SETUP Variables ************************
// Hardware-specific motor calibration constants.
// Run calibration program (______________.name) at startup, then update these constants with the calibration results.
// NOTE: The calibration softwares are notoriously finnicky, please run it multiple times and take the average. Also free feel to adjust these values and try multiple offsets.
// One can also discover their motor pole pair number by following this tutorial from SimpleFOC: https://docs.simplefoc.com/example_from_scratch. Match 1 rotation per 1 second in Step 2 to accurately set pole pairs.
const float ZERO_ELECTRICAL_OFFSET = 0.20;
static const Direction FOC_DIRECTION = Direction::CW;
static const int MOTOR_POLE_PAIRS = 7;
// ####

// PIN NUMBERS
//Magentic Sensor Pins
static const int NCS_PIN = 5; // some digital pin that you're using as the nCS pin

// Motor Driver Board Pins
static const int UH_PIN = 32;
static const int UL_PIN = 33;
static const int VH_PIN = 25;
static const int VL_PIN = 26;
static const int WH_PIN = 27;
static const int WL_PIN = 14;

// Button Pin
static const int buttonPin = 22;

// LED Pins
const int ledRed = 13;         // the PWM pin the Red LED is attached to
const int ledBlue = 4;         // the PWM pin the Blue LED is attached to
const int ledGreen = 12;         // the PWM pin the Green LED is attached to

// ** RGB LED Setup Variables
const int colorRed[3] = {200,20,0};
const int colorOrange[3] = {150,210,48};
const int colorYellow[3] = {100,250,25};
const int colorGreen[3] = {20,250,50};
const int colorCyan[3] = {30,220,250};
const int colorBlue[3] = {0,70,250};
const int colorMagenta[3] = {120,50,150};
const int colorPurple[3] = {110,0,250};
const int colorLightWhite[3] = {15, 25, 20};
const int colorBlack[3] = {0,0,0};
int activeColor[3];
//int lightIncrement = 0;

// RTC Stuff
time_t now;
struct tm timeInfo;

//Data Output Setups
//Storage - For easier processing and output within a single "print" statement (important to ensure quick processing of data monitoring loop so we don't mess up knob function)
char dataString[45];  // holds the data to be written to the file
// Variables for later averaging and printing to serial (and thereby document)
float motorAngleOutput;
float motorVelocityOutput;
float motorPhaseA;
float motorPhaseB;
float motorPhaseC;
int counter;
int countMax;

// Device Mode and Haptics Configuration
int configSelect = 1;
float config[7];
int readBuffer = 0;
int pinState = 0;
int formerPinState = 0;

static const float DEAD_ZONE_DETENT_PERCENT = 0.2;
static const float DEAD_ZONE_RAD = 1 * _PI / 180;

static const float IDLE_VELOCITY_EWMA_ALPHA = 0.001;
static const float IDLE_VELOCITY_RAD_PER_SEC = 0.05;
static const uint32_t IDLE_CORRECTION_DELAY_MILLIS = 500;
static const float IDLE_CORRECTION_MAX_ANGLE_RAD = 5 * PI / 180;
static const float IDLE_CORRECTION_RATE_ALPHA = 0.0005;

// magnetic sensor instance - SPI
MagneticSensorMT6701SSI sensor(NCS_PIN);

// BLDC motor & driver instance
BLDCMotor motor = BLDCMotor(MOTOR_POLE_PAIRS);
BLDCDriver6PWM driver = BLDCDriver6PWM(UH_PIN, UL_PIN, VH_PIN, VL_PIN, WH_PIN, WL_PIN);

// Set initial 2-detent mode
float current_detent_center = motor.shaft_angle;
float StartupMode[] = { 0, 0, (10 * PI / 180), 0, 1, 1.1, 1};  //free spinning with no detents
  // **STRUCTURE OF DETENT PARAMETER ARRAY**
  // int32_t num_positions; 0
  // int32_t position; 1
  // float position_width_radians; 2
  // float detent_strength_unit; 3
  // float endstop_strength_unit; 4
  // float snap_point; 5
  // float array identifier 6

float idle_check_velocity_ewma = 0;
uint32_t last_idle_start = 0;
uint32_t last_publish = 0;


void setup() {
  _delay(2000);
  // use monitoring with serial for motor init
  // monitoring port
  Serial.begin(115200);
  _delay(2000);

  // Configure LED Pins
  pinMode(ledRed, OUTPUT);
  pinMode(ledBlue, OUTPUT);
  pinMode(ledGreen, OUTPUT);

  // CONFIGURATE HARDWARE LINKS
  // initialise magnetic sensor hardware
  sensor.init();
  // link the motor to the sensor
  motor.linkSensor(&sensor);
  // driver config
  // power supply voltage [V]
  driver.voltage_power_supply = 10; //Set to your power supply voltage if you are using something different than prescribed. No need to supply more than 10V, really.
  driver.init();
  // link driver
  motor.linkDriver(&driver);

  // CONFIG FOC CONTROLS AND MODULATION
  // choose FOC modulation
  motor.foc_modulation = FOCModulationType::SpaceVectorPWM;
  // set control loop type to be used
  //motor.torque_controller = TorqueControlType::foc_current;
  motor.controller = MotionControlType::torque;

  // INITIALIZE FOC MOTOR
  // initialise motor
  motor.init();
  // align encoder and start FOC
  motor.initFOC(ZERO_ELECTRICAL_OFFSET, FOC_DIRECTION);
  // set the inital target value
  motor.target = 2;
  Serial.println("Just initialized the FOC");

  // INITIALIZE MOTOR MONITORING
  // tell the motor to use the monitoring **************************** Commented out for custom implementation.
  //motor.useMonitoring(Serial);
  // chosen variables to include in monitoring, were the standard library to be used.
  motor.monitor_variables = _MON_TARGET | _MON_VOLT_Q | _MON_VEL | _MON_ANGLE;  // default _MON_TARGET | _MON_VOLT_Q | _MON_VEL | _MON_ANGLE
  motor.monitor_downsample = 100;                                               // default 10, downsample output to serial

  _delay(2000);
  // **Here you can adjust the number of samples that are taken and averaged per each data output. Currently 50 samples (at 1000Hz) are included in each data output.
  counter = 0;
  countMax = 50;
  motorAngleOutput = 0.0;
  motorVelocityOutput = 0.0;
  motorPhaseA = 0.0;
  motorPhaseB = 0.0;
  motorPhaseC = 0.0;

  motor.voltage_limit = 5; //If your motor is drawing too much current, lower the voltage limit (and tune the PID parameters)
  motor.velocity_limit = 10000;

  // THese PID parameters can be tuned using the SimpleFOC studio (and a separate program) or just adjusted manually and recompiled. As that is time consuming, utilize SimpleFOC Studio if you will be doing lots of tuning.
  // SimpleFOC Studio: https://docs.simplefoc.com/studio 
  motor.PID_velocity.P = 4;
  motor.PID_velocity.I = 0.01;
  motor.PID_velocity.D = 0.001;
  motor.PID_velocity.output_ramp = 10000;
  motor.PID_velocity.limit = 6;
  motor.LPF_velocity.Tf = 0.001;

  motor.pole_pairs = MOTOR_POLE_PAIRS;
  motor.move(0); // initial zeroing move, before setting the mode
  
  // RTC Stuff - this is all to enable a real-time clock for accurate data matching with real-world occurences, if that interests you. Needs some work still, but functions with inital, manually seeded start time (below).
  struct timeval tv;
  tv.tv_sec =	1674219600;  // enter UTC UNIX time (get it from https://www.unixtimestamp.com ) ***THIS CAN BE UPDATED BEFORE STARTING THE DEVICE TO TRACK THE REAL TIME. Future work will make this automatic/from system.
  settimeofday(&tv, NULL);

  // Set timezone to France (Europe/Paris or your own timezone, if you want)
  setenv("TZ", "CET-1CEST,M3.5.0/2,M10.5.0/ 3", 1); // https://www.gnu.org/software/libc/manual/html_node/TZ-Variable.html
  tzset();

  time(&now);
  localtime_r(&now, &timeInfo);
  Serial.print("The current time in Amsterdam is ");
  Serial.println(&timeInfo, "%H:%M:%S");
  //Serial.println(timeInfo.tm_sec);   //KEY FOR HOW TO ACCESS THE TIME INFO STRUCTURE
  //Serial.println(timeInfo.tm_min);
  //Serial.println(timeInfo.tm_hour);
  delay(1000);
  
  // setup button pin
  pinMode(buttonPin, INPUT);

  //populate configuration of the first haptic mode
  for (int h = 0; h < 7; h++) {
    config[h] = StartupMode[h];  //unbounded, no detents
  }


    // Update derivative factor of torque controller based on detent width.
    // If the D factor is large on coarse detents, the motor ends up making noise because the P&D factors amplify the noise from the sensor.
    // This is a piecewise linear function so that fine detents (small width) get a higher D factor and coarse detents get a small D factor.
    // Fine detents need a nonzero D factor to artificially create "clicks" each time a new value is reached (the P factor is small
    // for fine detents due to the smaller angular errors, and the existing P factor doesn't work well for very small angle changes (easy to
    // get runaway due to sensor noise & lag)).
    // TODO: consider eliminating this D factor entirely and just "play" a hardcoded haptic "click" (e.g. a quick burst of torque in each
    // direction) whenever the position changes when the detent width is too small for the P factor to work well.
    const float derivative_lower_strength = config[3] * 0.08;
    const float derivative_upper_strength = config[3] * 0.02;
    const float derivative_position_width_lower = radians(3);
    const float derivative_position_width_upper = radians(8);
    const float raw = derivative_lower_strength + (derivative_upper_strength - derivative_lower_strength) / (derivative_position_width_upper - derivative_position_width_lower) * (config[2] - derivative_position_width_lower);
    motor.PID_velocity.D = constrain(
      raw,
      min(derivative_lower_strength, derivative_upper_strength),
      max(derivative_lower_strength, derivative_upper_strength));

    Serial.print("This is the new D");
    Serial.println(motor.PID_velocity.D);   
    _delay(2500);

    //Flash green LED to show ready!
    for (int j = 0; j < 4; j++) {
      analogWrite(ledRed, (255-colorGreen[0]));
      analogWrite(ledGreen, (255-colorGreen[1]));
      analogWrite(ledBlue, (255-colorGreen[2]));
      delay(50);
      analogWrite(ledRed, (255));
      analogWrite(ledGreen, (255));
      analogWrite(ledBlue, (255));
      delay(50);
    }
    Serial.println("Ready!");
    delay(500);
    analogWrite(ledRed, (255-colorRed[0]));
    analogWrite(ledGreen, (255-colorRed[1]));
    analogWrite(ledBlue, (255-colorRed[2]));
}
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

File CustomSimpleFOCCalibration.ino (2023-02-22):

/* Adapted SmartKnob calibration program for my own motor as a standalone program within the Arduino IDE
*/

#include <SimpleFOC.h>
#include "Arduino.h"
#include <vector>
#include "SimpleFOCDrivers.h"
#include "encoders/MT6701/MagneticSensorMT6701SSI.h"

// magnetic sensor instance - SPI
#define SENSOR1_CS 5  // some digital pin that you're using as the nCS pin
MagneticSensorMT6701SSI sensor(SENSOR1_CS);

// BLDC motor & driver instance
BLDCMotor motor = BLDCMotor(1);
BLDCDriver6PWM driver = BLDCDriver6PWM(32, 33, 25, 26, 27, 14); //THE U, V, AND W PHASE PINS FROM THE MAIN PROGRAM

int runCheck;
float a = 0.0;

void setup() {
  // put your setup code here, to run once:
  runCheck = 0;
  _delay(1000);
  Serial.begin(115200);
  
  //Initialize magnetic sensor
  sensor.init();

  // link driver
  driver.voltage_limit = 4.5;
  driver.voltage_power_supply = 10;

  driver.init();
  
  motor.linkDriver(&driver);
  // link the motor to the sensor
  motor.linkSensor(&sensor);

  // choose FOC modulation
  //motor.foc_modulation = FOCModulationType::SpaceVectorPWM;
  motor.controller = MotionControlType::angle_openloop;
  motor.pole_pairs = 1;

  //initialize motor
  motor.init();
  motor.initFOC(0, Direction::CW);
  //motor.initFOC();
}


void MotorCalibrate() {
    while (runCheck < 1) {
      // SimpleFOC is supposed to be able to determine this automatically (if you omit params to initFOC), but
      // it seems to have a bug (or I've misconfigured it) that gets both the offset and direction very wrong!
      // So this value is based on experimentation.
      // TODO: dig into SimpleFOC calibration and find/fix the issue

      _delay(3000);
      Serial.println("Starting calibration, please DO NOT TOUCH MOTOR until complete!");

      // #### Determine direction motor rotates relative to angle sensor
      for (uint8_t i = 0; i < 200; i++) {
          sensor.update();
          motor.move(a);
          delay(1);
      }
      Serial.println("Sensor moved to 0");
      float start_sensor = sensor.getAngle();
      Serial.println(start_sensor);

      for (a; a < (3 * _2PI); a += 0.01) {
          sensor.update();
          motor.move(a);
          delay(1);
      }

      for (uint8_t i = 0; i < 200; i++) {
          sensor.update();
          delay(1);
      }
      float end_sensor = sensor.getAngle();
      Serial.println(end_sensor);


      motor.voltage_limit = 5;
      motor.move(a);

      Serial.println("");

      // TODO: check for no motor movement!

      Serial.println("Sensor measures positive for positive motor rotation:");
      if (end_sensor > start_sensor) {
          Serial.println("YES, Direction=CW");
          motor.initFOC(0, Direction::CW);
      } else {
          Serial.println("NO, Direction=CCW");
          motor.initFOC(0, Direction::CCW);
      }
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

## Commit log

2023-02-21 Including CAD files for Fidget Knob (v1)
    [ElectronicsBox.SLDASM, FK_AssmBasePlate.SLDPRT, FK_AssmPeg.SLDPRT, FK_BLDCMount.SLDPRT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]
2023-02-22 First code inclusion
    [ElectronicsBox.SLDASM, FK_AssmBasePlate.SLDPRT, FK_AssmPeg.SLDPRT, FK_BLDCMount.SLDPRT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]
2023-03-08 Second big content update
    [ElectronicsBOM.xlsx, ElectronicsBox - FK_ButtonArm-1.STL, ElectronicsBox - FK_ElectronicsBox-1.STL, ElectronicsBox - FK_ElectronicsLid-1.STL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]
2023-03-09 First prod. version of main and calibration code
